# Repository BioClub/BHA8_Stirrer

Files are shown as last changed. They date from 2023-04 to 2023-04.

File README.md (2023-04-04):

## BHA Stirrer
This repo contains the designs and source files of a **DIY Magnetic Stirrer**. Such a device is used to stir liquids continiously for a long period of time. The optional heating pad keeps the liquid warm, it is not design for boiling or cooking.

- This repo is a clone from https://gitlab.waag.org/biohack/BHA_Stirrer, please go there for the history and provenience. 
- `BoM` will be specific to Japan.
- We will also described more `hacky` ways (old computer fans, etc) to build the Stirrer.

## Navigation the repo

 	BHA_Stirrer/				main repo
 	|-- Magnetic-Stirrer-kicad/		wiring documentation
 	BoM.md					Bill of Materials
 	Magnetic-Stirrer-Cut-Sheet-3mm.svg	Laser cut sheet 3mm
 	Magnetic-Stirrer-Cut-Sheet-4mm.svg	Laser cut sheet 4mm
 	Magnetic-Stirrer.f3d			Fusion 360 model

## Releases

The magnetic stirrer v4.0 release contains the following:

* 2023 BHA8 Design

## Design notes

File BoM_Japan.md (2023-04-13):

## Bill of Materials

For this device you do not need an Arduino or equivalent microprocessor.

Do make sure you have enough 3mm material to cut the design from and a bunch of M3 10mm and 30mm bolts and nuts for the assembly.

### Must have

|Quantity|Part|Link|Unit price|
|--------|----|----|----------|
|1       |Fan|[12V 92 x 92mm Fab](https://akizukidenshi.com/catalog/g/gP-14359/) or something similar|~¥400|
|1       |Metal Plate Circle, 0,5mm thick, diameter 90mm|[Tokyu Hands](https://hands.net/) or something similar|~¥300|
|5       |Magnetic Stirring Rods|[Monotaro](https://www.monotaro.com/p/4046/8741/)|¥1,634|
|2       |Permanent Magnets|Daiso (Pack of 8)|¥110|
|4       |Rubber Feet|[Monotaro](https://www.monotaro.com/p/0933/2574/?t.q=rubber%20feet)|¥34|
|1       |Power Switch|[Akizuki](https://akizukidenshi.com/catalog/g/gP-15740/)|¥100|
|1       |2.1mm DC power Jack|[Akizuki](https://akizukidenshi.com/catalog/g/gC-17108/)|¥50|
|1       |Heating Foil 12V 22W|[Akizuki](https://akizukidenshi.com/catalog/g/gP-14812/)|¥800| 
|1       |7.5W - power supply (1000mA)| | |
|1       |Potentiometer 100Ω 2W|[Digikey](https://www.digikey.jp/en/products/detail/bourns-inc/93R1A-R22-A05L/2564715?s=N4IgTCBcDaIJwGYBOBGAhgWiWMG0AYBWAGxAF0BfIA)|¥1,171|
|1       |Potentiometer 100KΩ 0.2W|[Digikey](https://www.digikey.jp/en/products/detail/bourns-inc/PDB181-K420P-104B/3820299) - not available|¥111|
|1       |FR-1 Single-Sided Copper Board| | |
|1       |2.2uF Capacitor (C1)|[Digikey](https://www.digikey.jp/en/products/detail/samsung-electro-mechanics/CL31B225KOHNNNE/3886922)|¥25|
|1       |100nF (=0.1uF) Capacitor (C2) 3216|[Akizuki](https://akizukidenshi.com/catalog/g/gP-15180/), Pack of 5|¥120|
|1       |Schottky Diode 100V 1A (D3)|[Akizuki](https://akizukidenshi.com/catalog/g/gI-06189/), Pack of 20|¥250|
|2       |Zener Diode (D_Z1, D_Z2) BZT52C3V3, SOD-123 3.3V 0.5W|[Digikey](https://www.digikey.jp/en/products/detail/yangjie-technology/BZT52C3V3/16734164)| |
|4       |Terminal Block 2.54mm 2P|[Akizuki](https://akizukidenshi.com/catalog/g/gP-14217/)|¥25|
|2       |Terminal Block 2.54mm 3P|[Akizuki](https://akizukidenshi.com/catalog/g/gP-14612/)|¥30|
|1       |MOSFET_N-CH_30V_1.7A|[Digikey](https://www.digikey.jp/en/products/detail/alpha-omega-semiconductor-inc/AO7400/1855856), Alternative [Akizuki](https://akizukidenshi.com/catalog/g/gI-06049/)| |
|1       |470Ω      3216|[Sengoku](https://www.sengoku.co.jp/mod/sgk_cart/detail.php?code=EEHD-0ECL), Pack of 10|¥53|
|2       |1KΩ       3216|[Sengoku](https://www.sengoku.co.jp/mod/sgk_cart/detail.php?code=EEHD-0ECV), Pack of 10|¥53|
|1       |100kΩ     3216|[Digikey](https://www.digikey.jp/en/products/detail/stackpole-electronics-inc/RMCF1206FT100K/1759689)|¥14|
|2       |0Ω Jumper 3216|[Digikey](https://www.digikey.jp/en/products/detail/yageo/RC1206JR-070RL/729184)|¥14|
|1       |NE555D Timer (SMD)|[Akizuki](https://akizukidenshi.com/catalog/g/gI-16210/)|¥30|

**Alternatives**

* You could use all kind of motors, for example from a hard drive.
* Take a USB coffee mug heater apart for the heating foil or use a cheap power resistor to save money

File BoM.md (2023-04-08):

## Bill of Materials

For this device you do not need an Arduino or equivalent microprocessor. Do make sure you have enough 3mm material to cut the design from and a bunch of M3 10mm and 30mm bolts and nuts for the assembly.

### Must have

|Quantity|Part                                          |Link                                                                                                                                         |Unit price|FIELD5|
|--------|----------------------------------------------|---------------------------------------------------------------------------------------------------------------------------------------------|----------|------|
|1       |80 mm Fan                                     |https://www.digikey.nl/nl/products/detail/mechatronics-fan-group/F8025M12B-FSR/5209759                                                       |� 10,02   |      |
|1       |metal plate circle, 0,5mm thick, diameter 90mm|https://www.combicraft.nl/toiletbordje-toiletten.html                                                                                        |� 2,99    |      |
|1       |Magnetic stirring rod                         |                                                                                                                                             |          |      |
|1       |Permanent magnets                             |                                                                                                                                             |          |      |
|4       |Rubber feet                                   |https://www.conrad.nl/nl/p/toolcraft-2210sw12-c-apparaatvoet-zelfklevend-rond-zwart-x-h-22-3-mm-x-10-1-mm-12-stuk-s-1339867.html             |� 4,99    |      |
|1       |Power switch                                  |                                                                                                                                             |          |      |
|1       |DC power jack                                 |https://www.digikey.nl/nl/products/detail/kycon-inc/KLDPLX-0202-A/12627588                                                                   |� 1,89    |      |
|1       |Heating foil 12V 22W                          |https://www.conrad.nl/nl/p/thermo-tech-polyester-verwarmingsfolie-zelfklevend-12-v-dc-12-v-ac-22-w-beschermingsklasse-ipx4-90-mm-1216623.html|� 20,99   |      |
|1       |7.5 W power supply (1000mA)                   |                                                                                                                                             |� 0,10    |      |
|1       |Potentiometer 100 ohm 2W                      |https://www.digikey.nl/nl/products/detail/bourns-inc/93R1A-R22-A05L/2564715                                                                  |� 7,88    |      |
|1       |Potentiometer 100 Kohm 2W                     |https://www.digikey.nl/nl/products/detail/bourns-inc/PDB181-K420P-104B/3820299                                                               |� 1,00    |      |
|1       |PCB plate                                     |https://eu.robotshop.com/products/4-6-fr1-copper-clad-single-sided-10pk                                                                      |          |      |
|1       |2.2uF Capacitor (C1)                          |                                                                                                                                             |          |      |
|1       |100nF Capacitor (C2)                          |                                                                                                                                             |          |      |
|1       |Schottky Diode 100V 1A (D3)                   |                                                                                                                                             |          |      |
|2       |Zener Diode (D_Z1, D_Z2)                      |https://www.digikey.nl/nl/products/detail/yangzhou-yangjie-electronic-technology-co-ltd/BZT52C3V3/13911636|          |      |
|4       |Screw_Terminal_01x02_P3.5mm                   |                                                                                                                                             |          |      |
|2       |Screw_Terminal_01x03_P3.5mm                   |                                                                                                                                             |          |      |
|1       |MOSFET_N-CH_30V_1.7A                          |https://www.digikey.nl/nl/products/detail/onsemi/NDS355AN/458899?s=N4IgTCBcDaIHYBMDOBmArGghnAxgFwFpEQBdAXyA|          |      |
|1       |470                                           |                                                                                                                                             |          |      |
|2       |1k                                            |                                                                                                                                             |          |      |
|1       |100k                                          |                                                                                                                                             |          |      |
|2       |0                                             |                                                                                                                                             |          |      |
|1       |NE555D Timer (SMD)                            |                                                                                                                                             |          |      |

**Alternatives**

* You could use all kind of motors, for example from a hard drive.
* Take a USB coffee mug heater apart for the heating foil or use a cheap power resistor to save money

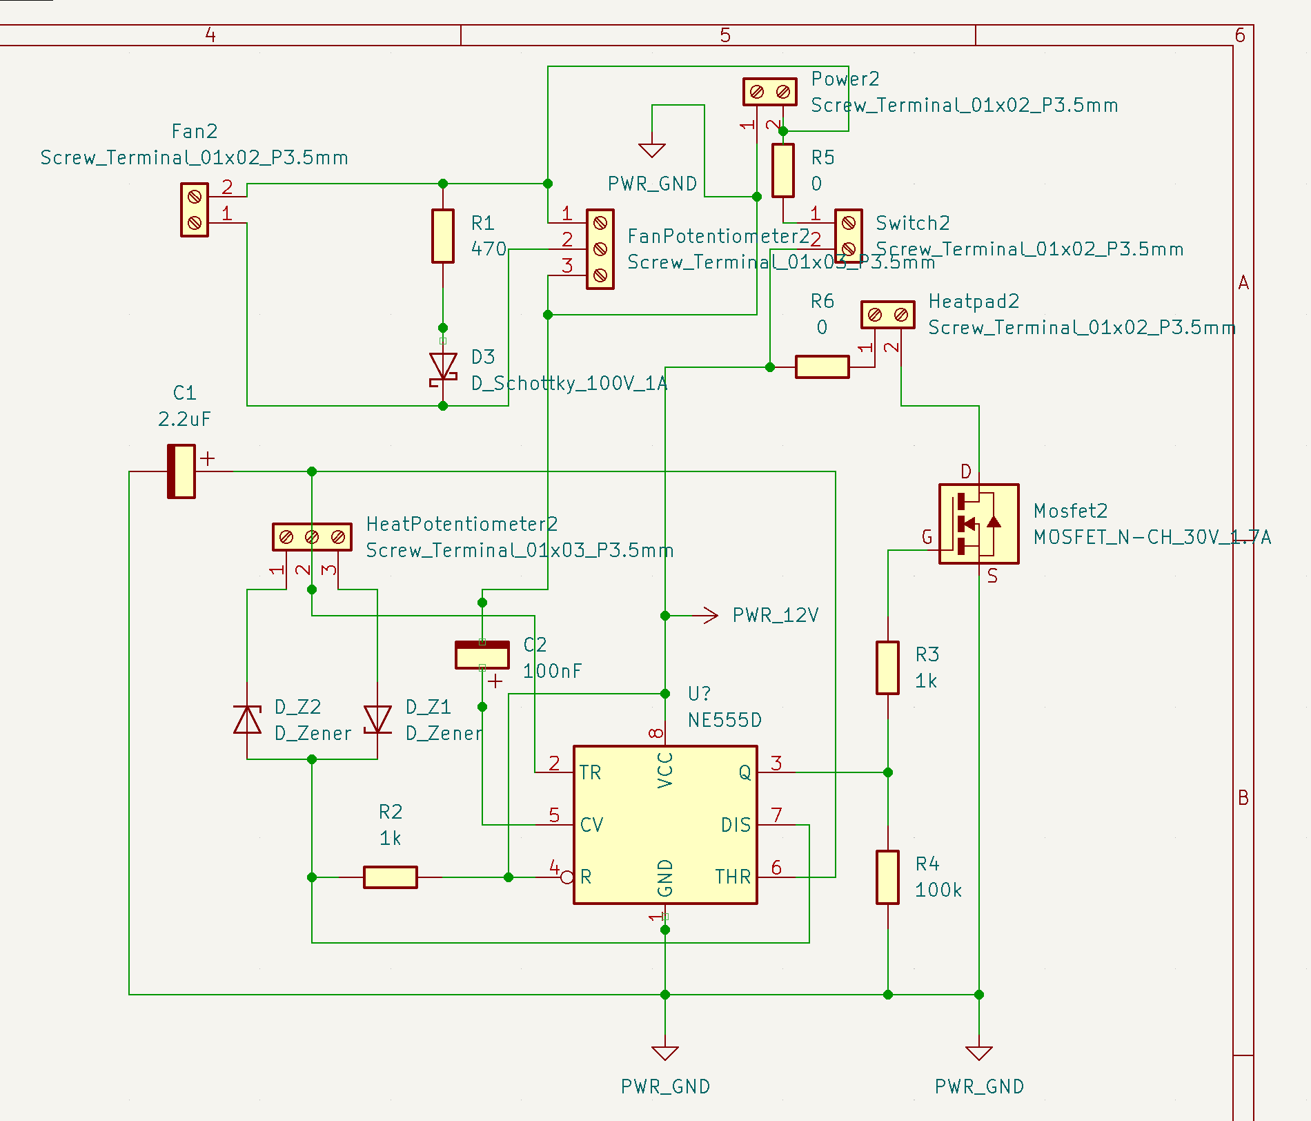
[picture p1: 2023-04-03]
circuit_.png

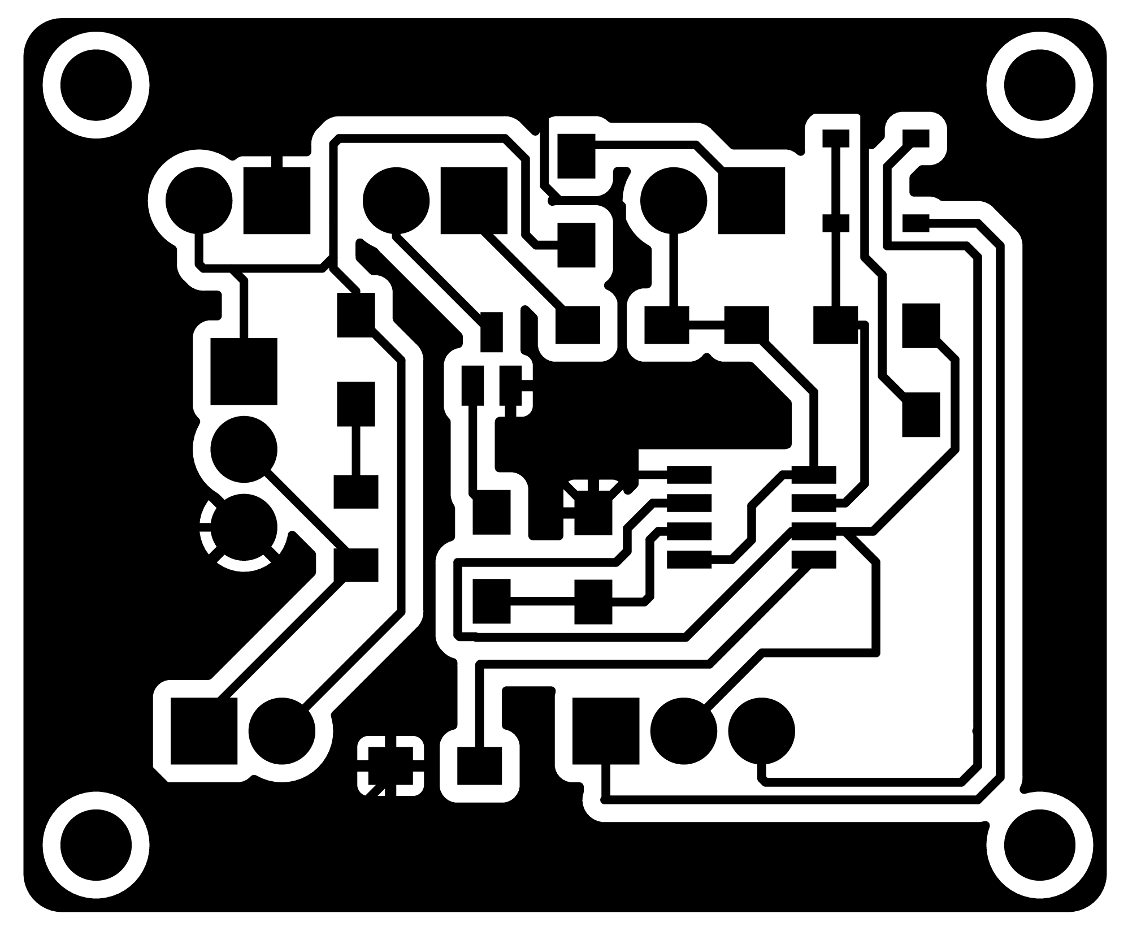
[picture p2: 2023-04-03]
Magnetic-Stirrer-kicad/SMD-Magnetic-Stirrer-inner.png

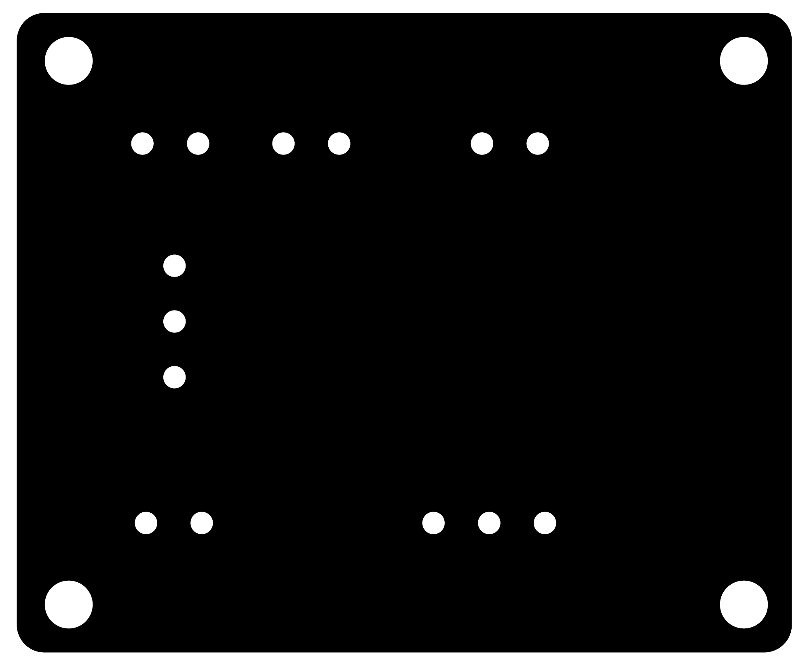
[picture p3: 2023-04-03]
Magnetic-Stirrer-kicad/SMD-Magnetic-Stirrer-outer.png

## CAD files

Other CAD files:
Magnetic-Stirrer.f3d

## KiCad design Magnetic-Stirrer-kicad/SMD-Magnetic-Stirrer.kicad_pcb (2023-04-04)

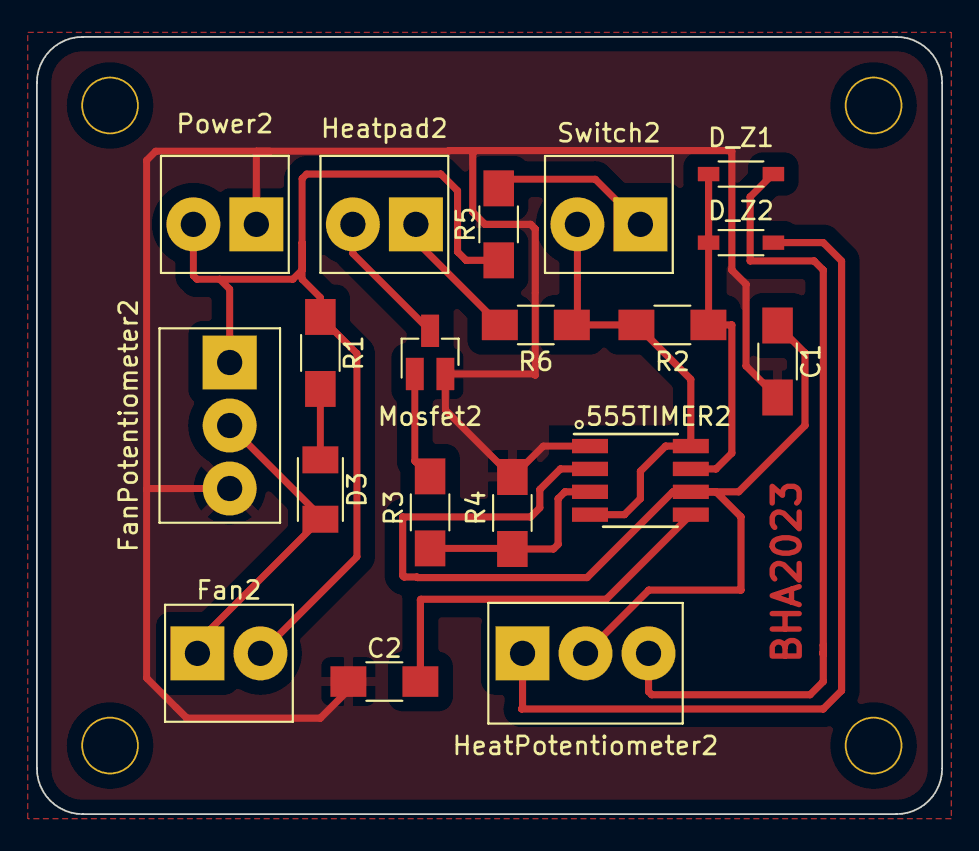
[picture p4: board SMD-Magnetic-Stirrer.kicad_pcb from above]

Board: 2 copper layers, 50.3 x 43.2 mm, 19 parts (0 on the bottom side), 15 nets.

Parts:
555TIMER2: NE555P; SOIC-8_3.9x4.9mm_P1.27mm
C1: 2.2uF; C_1206
C2: 100nF; C_1206
D3: D_Schottky_100V_1A; SOD-123T
D_Z1, D_Z2: D_Zener; SOD-123
Fan2: Screw_Terminal_01x02_P3.5mm; TerminalBlock_OnShore_1x02_P3.50mm_Horizontal
FanPotentiometer2: Screw_Terminal_01x03_P3.5mm; TerminalBlock_OnShore_1x03_P3.50mm_Horizontal
HeatPotentiometer2: Screw_Terminal_01x03_P3.5mm; TerminalBlock_OnShore_1x03_P3.50mm_Horizontal
Heatpad2: Screw_Terminal_01x02_P3.5mm; TerminalBlock_OnShore_1x02_P3.50mm_Horizontal
Mosfet2: MOSFET_N-CH_30V_1.7A; SOT-23
Power2: Screw_Terminal_01x02_P3.5mm; TerminalBlock_OnShore_1x02_P3.50mm_Horizontal
R1: 470; R_1206
R2, R3: 1k; R_1206
R4: 100k; R_1206
R5, R6: 0; R_1206
Switch2: Screw_Terminal_01x02_P3.5mm; TerminalBlock_OnShore_1x02_P3.50mm_Horizontal

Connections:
unnamed: 555TIMER2.3 (Q), R3.2, R4.1
unnamed: 555TIMER2.5 (CV), C2.2
unnamed: 555TIMER2.4 (R), 555TIMER2.8 (VCC), R2.2, R6.1, Switch2.2
unnamed: 555TIMER2.2 (TR), 555TIMER2.6 (THR), C1.1, HeatPotentiometer2.2
unnamed: D3.2 (A), R1.2
unnamed: D_Z2.1 (K), HeatPotentiometer2.1
unnamed: 555TIMER2.7 (DIS), D_Z1.1 (K), D_Z2.2 (A), R2.1
unnamed: D3.1 (K), Fan2.1, FanPotentiometer2.2
unnamed: D_Z1.2 (A), HeatPotentiometer2.3
unnamed: Heatpad2.1, R6.2
unnamed: Heatpad2.2, Mosfet2.3 (D)
unnamed: Fan2.2, FanPotentiometer2.1, Power2.2, R1.1, R5.1
unnamed: Mosfet2.1 (G), R3.1
unnamed: R5.2, Switch2.1
PWR_GND: 555TIMER2.1 (GND), C1.2, C2.1, FanPotentiometer2.3, Mosfet2.2 (S), Power2.1, R4.2

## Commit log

2023-04-03 Clone from Waag's GitLab
    Clone from Waag's GitLab https://gitlab.waag.org/biohack/BHA_Stirrer
    [Magnetic-Stirrer.f3d, SMD-Magnetic-Stirrer.kicad_pcb, SMD-Magnetic-Stirrer.kicad_sch]
2023-04-04 KiCAD Latest
    [SMD-Magnetic-Stirrer.kicad_pcb, SMD-Magnetic-Stirrer.kicad_sch]
